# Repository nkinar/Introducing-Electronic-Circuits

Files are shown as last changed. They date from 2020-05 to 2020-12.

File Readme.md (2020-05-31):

# Introducing Electronic Circuits and Hydrological Models to Postsecondary Physical Geography Students: Systems Science, Circuit Theory, Construction and Calibration
## by Nicholas J. Kinar
*Journal of Geoscience Communication (GC)*

## What is it?

* The download contains directories providing circuit board design files and feedback data.
Files are provided "as is" and should be checked before use in a specific application.

* Please see the associated paper for additional information.  

* Cost and part numbers in the Excel bill of material (BOM) spreadsheets are current at the time of
writing.  The cost is in Canadian dollars.  Most part numbers for passive components (resistors and capacitors)
can be substituted.  The BOM does not include materials used for kit packaging: ESD bags, plastic bags and
ESD foam used to protect IC pins.

* Bags, labelling machines and labels can be sourced from Uline (or a similar supplier):
<https://www.uline.ca/> or
<https://www.uline.com/>

* At the time of writing, an educational license is available from Altium and
the DFM Now! software can be downloaded as a no-cost license.  See the table
below for further details.

* All circuit board designs are licensed under the open hardware CERN OHL license:
http://cern.ch/cern-ohl

* All source code is provided under the GNU GPL v3:
https://www.gnu.org/licenses/gpl-3.0.en.html

## FILES

Bolded entries in the table indicate parent directories.  Non-bolded
entries indicate subdirectories.

| Directory   |     Description  |
|----------|:-------------:|
| **class-sensor-pcb-design-files** | Parent directory with design files for the class RH/temperature/pyranometer circuit|
| altium |   Design files in Altium designer format (https://www.altium.com/)  |  
| bom | Bill of Materials (Excel) |
|code	| Code for Atmel AVR microcontroller (Atmel Studio)|
|gerber	| Gerber files |
|schematic	| Schematic (PDF) |
|**feedback data**	| Directory with in-class feedback|
|**feedback-data-sleq**	| Feedback data from the SLEQ survey|
|**water-sensor-pcb-design-files**	| Directory with design files for the class water detection circuit|
|altium	|						Design files in Altium designer format (https://www.altium.com/)|
|bom |								Bill of Materials (Excel)|
|gerber |							Gerber files|
|schematic |						Schematic (PDF)|

## GERBER FILES README AND MAPPING

1.	These are 2 layer PCBs.
2.	Round up drill size to the next available drill (free or non-free) if required.
3.	Soldermask on both sides of the PCB
4.	Silkscreen on both sides of the PCB
5.	DFM Now! software can be used for Gerber preview (https://www.numericalinnovations.com/)
6.	gerbv also works well as Gerber preview software (http://gerbv.sourceforge.net/)

| Layer Extension   |     Layer Description  |
|----------|:-------------:|
|.GTO|                Top Overlay |                            
|.GTS|                Top Solder  |                            
|.GTL|                Top Layer    |                           
|.GBL|                Bottom Layer      |                      
|.GBS|                Bottom Solder   |                        
|.GM1|                Mechanical 1   |                         
|.GPT|                Top Pad Master      |                    
|.GPB|                Bottom Pad Master|
|.DRR| 				NC Drill File Report|
|.TXT|				NC Drill File|

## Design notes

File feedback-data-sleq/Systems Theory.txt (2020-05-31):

While I a still confused about it, I think it is good knowledge to know.

I can see better connection between different processes involved in evironal sciences

Environmental sciences are all about systems. Because of this class I think broader now when reviewing a system.

I see systems theory as an integral framework of how we understand natural phenomena in that it is how we can turn readings
from instruments and synthesize them into models that describe a natural system with distinct boundary conditions and specific
inputs.

It's important to understand every component of the environment with great detail. You can use these systems as sub systems to
understand the greater picture.

very important

Understanding systems and the theory behind how they work is important to understanding the natural environment for a variety of
environmental studies.

I never thought about the importance of these systems before this class, so I suppose it opened my eyes to the complexity of
research

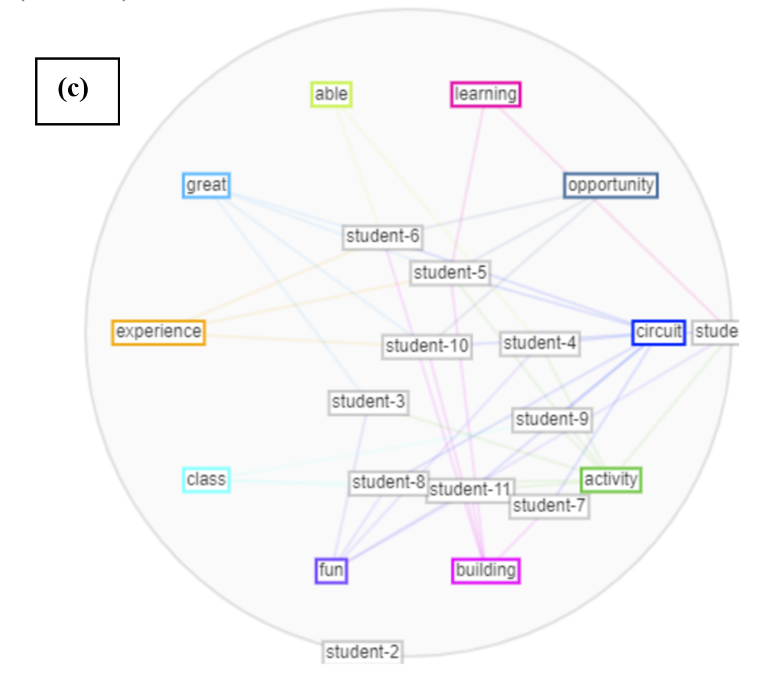
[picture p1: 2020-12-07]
feedback-data/mandala.PNG

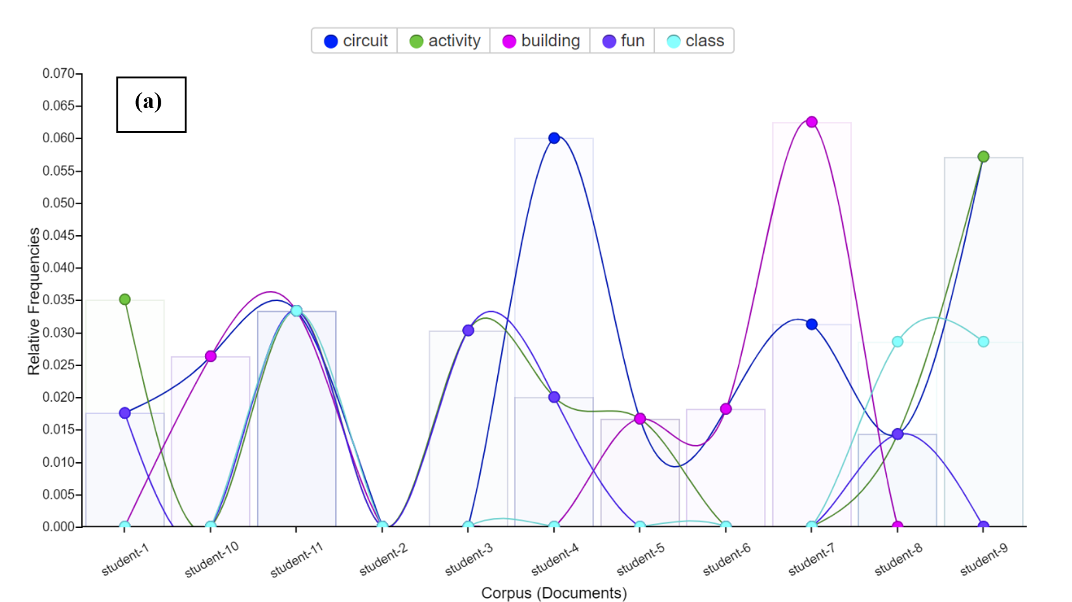
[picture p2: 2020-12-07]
feedback-data/trends.PNG

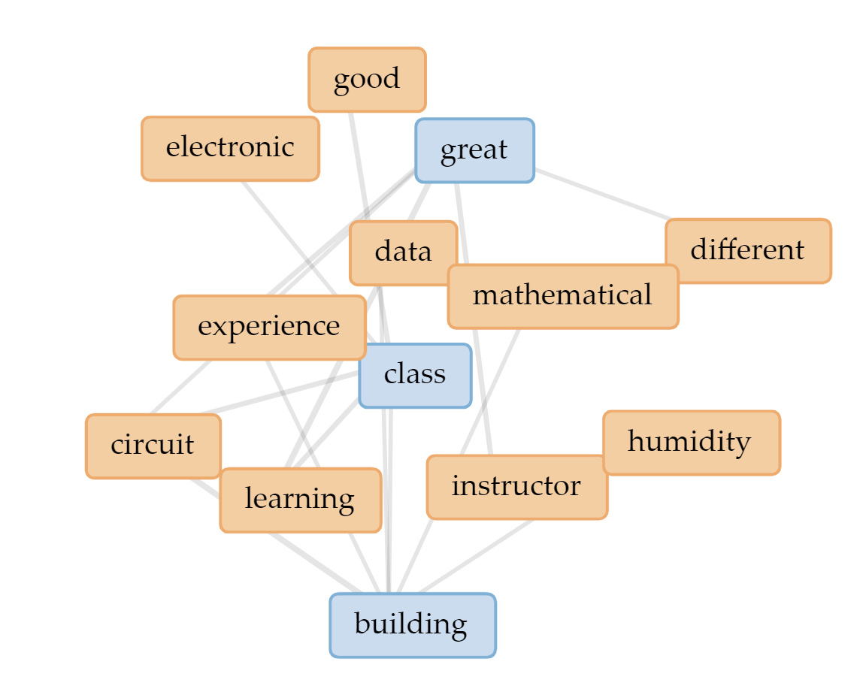
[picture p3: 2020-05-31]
feedback-data-sleq/links.PNG

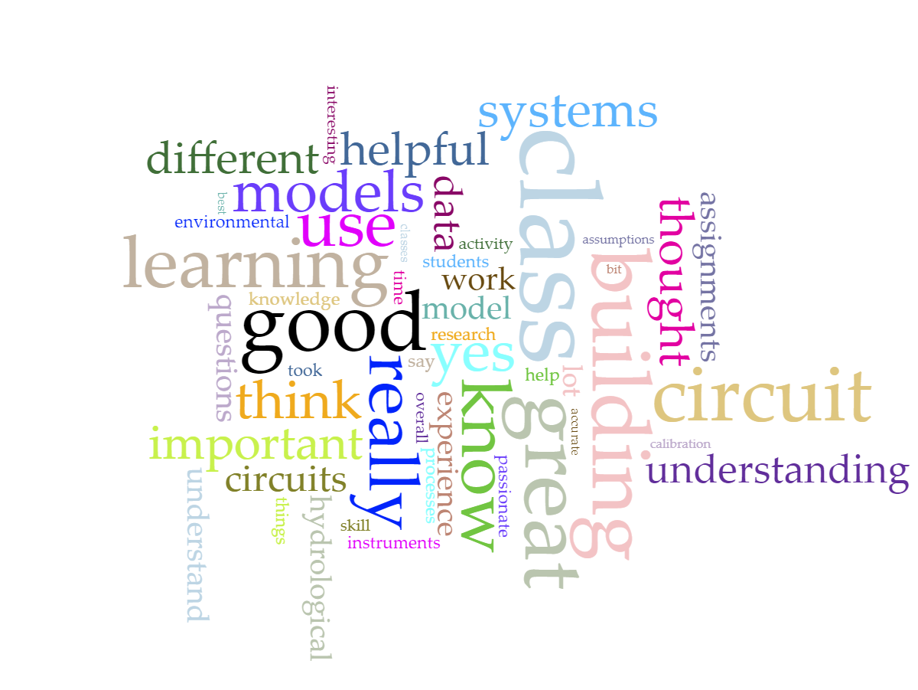
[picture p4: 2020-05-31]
feedback-data-sleq/cirrus.PNG

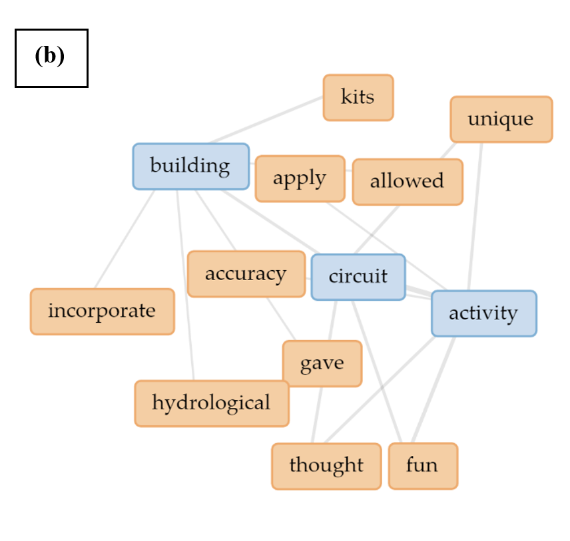
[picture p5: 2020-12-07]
feedback-data/links.PNG

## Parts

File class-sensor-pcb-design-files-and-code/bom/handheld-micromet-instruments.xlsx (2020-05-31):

Line # | Qty | Manufacturer P/N | Manufacturer | Distributor P/N | Distributor | Description
1 | 1 | BK Precision 725 | BK Precision | BK725-ND | Digikey.ca | Humidity/Temperature Meter
2 | 1 | TPI 565C1 | TPI (Test Products Int) | 290-1975-ND | Digikey.ca | Hot wire anemometer / Temperature Meter
3 | 1 | SP505 | Extech | SP505-ND | Digikey.ca | Solar power (flux) Meter
4 | 1 | SD-1128 | Reed Instruments | B008S0AKJA | Amazon.ca | Light meter

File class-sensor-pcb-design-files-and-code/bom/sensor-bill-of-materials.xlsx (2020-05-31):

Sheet: Totals
Qty | 30
 |  | Currency
Option 1 | Relative Humidity and Temperature
Base Cost | 16.97 | CND
Relative Humidity | 8.01 | CND
TOTAL per student | $24.98 | CND
Option 2 | Pyranometer
Base Cost | 16.97 | CND
Pyranometer Sensor | 13.59 | CND
TOTAL per student | $30.56 | CND
Option 3 | Both RH/T and Pyranometer
Base Cost | 16.97 | CND
Both Sensors | 22.2 | CND
TOTAL per student | $39.17 | CND
Tools and Materials
TOTAL | $156.20 | CND
PCBs
TOTAL | $66.60 | CND

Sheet: Base Kit
Line # | Designator | Qty | Total Order | Manufacturer P/N | Manufacturer | Total | Distributor P/N | Distributor | Description | Unit Cost (CND) | Total Cost (CND) | Comments | Price per package | Currency Conversion | Package (CND) | Total Number | Cost per unit (CND)
1 | U1 | 1 | 0 | ERM802SN-1 | EastRising | 0 | ERM802SN-1 | buydisplay.com | LCD Display | 2.75 | 2.75 | LCD display | 2.07 | 1.33 | 2.7531 | 1 | 2.75
2 | NA | 1 | 0 | B0784FMY9J | abcGOODefg | 0 | B0784FMY9J | Amazon.ca | 9V battery holder | 1.75 | 1.75 | Holds 9V battery on PCB | 13.99 | 1 | 13.99 | 8 | 1.75
3 | NA | 1 | 0 | PCB | allpcb.com | 0 | PCB | allpcb.com | Custom PCB for circuit | 2.22 | 2.22 | PCB for circuit | 50 | 1.33 | 66.5 | 30 | 2.22
4 | NA | 1 | 0 | Battery | Amazon Basics | 0 | B00MH4QM1S | Amazon.ca | 9v Battery | 1.66 | 1.66 | Battery to run circuit
5 | C1,C16,C17 | 3 | 0 | ECE-A1HKS100 | Panasonic Electronic Components | 0 | P997-ND | Digikey | CAP ALUM 10UF 20% 50V RADIAL | 0.04 | 0.13 | Decoupling capacitor
6 | C2,C3,C4 | 3 | 0 | A104K15X7RF5TAA | Vishay BC Components | 0 | 1109PHCT-ND | Digikey | CAP CER 0.1UF 50V X7R AXIAL | 0.24 | 0.71 | Decoupling capacitor
7 | R1 | 1 | 0 | 3306P-1-502 | Bourns Inc. | 0 | 3306P-502-ND | Bourns | TRIMMER 5K OHM 0.2W PC PIN TOP | 0.55 | 0.55 | Trimpot for LCD contrast
8 | R2,R3,R4 | 3 | 0 | CF14JT10K0 | Stackpole Electronics Inc | 0 | CF14JT10K0CT-ND | Digikey | RES 10K OHM 1/4W 5% AXIAL | 0.03 | 0.10 | Pullup resistors
9 | L1 | 1 | 0 | 78F100J-TR-RC | Bourns Inc. | 0 | 78F100J-TR-RCCT-ND | Digikey | FIXED IND 10UH 370MA 750 MOHM TH | 0.40 | 0.40 | Inductor for LC filter
10 | U6 | 1 | 0 | ATMEGA168PA-PU | Microchip Technology | 0 | ATMEGA168PA-PU-ND | Digikey | IC MCU 8BIT 4KB FLASH 28DIP | 2.50 | 2.50 | Microcontroller
11 | C5,C7 | 2 | 0 | K330J15C0GF5TH5 | Vishay BC Components | 0 | BC1036CT-ND | Digikey | CAP CER 33PF 50V C0G/NP0 RADIAL | 0.25 | 0.50 | Crystal resonator circuit capacitors
12 | X1 | 1 | 0 | ATS080B-E | CTS-Frequency Controls | 0 | CTX917-ND | Digikey | CRYSTAL 8.0000MHZ 18PF T/H | 0.48 | 0.48 | Crystal for microcontroller
13 | P2 | 1 | 0 | M20-9980346 | Harwin Inc. | 0 | 952-2121-ND | Digikey | CONN HEADER VERT 6POS 2.54MM | 0.33 | 0.33 | Programming header
14 | J2 | 1 | 0 | JS202011CQN | C&K | 0 | 401-2001-ND | Digikey | SWITCH SLIDE DPDT 300MA 6V | 0.60 | 0.60 | Power switch
15 | D2 | 1 | 0 | BAT85S-TAP | Vishay | 0 | BAT85S-TAPCT-ND | Digikey | DIODE SCHOTTKY 30V 200MA DO35 | 0.46 | 0.46 | Diode
16 | U13 | 1 | 0 | LP2950-50LPRE3 | Texas Instruments | 0 | 296-20933-1-ND | Digikey | IC REG LINEAR 5V 100MA TO92-3 | 0.61 | 0.61 | Linear regulator
18 | NA | 4 | 0 | 91772A057 | McMaster-Carr | 0 | 91772A057 | McMaster-Carr | #0 bolts for display | 0.10 | 0.40 | Bolts for display | 7.87 | 1.33 | 10.4671 | 100 | 0.1
19 | NA | 4 | 0 | 90107A001 | McMaster-Carr | 0 | 90107A001 | McMaster-Carr | #0 washer for display | 0.03 | 0.12 | Washer for display | 2.36 | 1.33 | 3.1388 | 100 | 0.03
20 | NA | 4 | 0 | 91841A115 | McMaster-Carr | 0 | 91841A115 | McMaster-Carr | #0 hex nut for display | 0.10 | 0.40 | Hex nut | 7.85 | 1.33 | 10.4405 | 100 | 0.1
21 | NA | 3 | 0 | 90353A486 | McMaster-Carr | 0 | 90353A486 | McMaster-Carr | M2 bolts for battery | 0.05 | 0.15 | Bolts for battery | 4.1 | 1.33 | 5.453 | 100 | 0.05
22 | NA | 3 | 0 | 91166A180 | McMaster-Carr | 0 | 91166A180 | McMaster-Carr | M2 washer for battery | 0.02 | 0.06 | Washer for battery | 1.57 | 1.33 | 2.0881 | 100 | 0.02
23 | NA | 3 | 0 | 90591A265 | McMaster-Carr | 0 | 90591A265 | McMaster-Carr | M2 hex nut for battery | 0.03 | 0.09 | Hex nut for battery | 2.08 | 1.33 | 2.7664 | 100 | 0.03
 |  |  |  |  |  |  |  |  |  | TOTAL | 16.97

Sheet: RH-T kit
Line # | Designator | Qty | Total Order | Manufacturer P/N | Manufacturer | Total Qty | Distributor P/N | Distributor | Description | Unit Cost (CND) | Total Cost (CND) | Comments | Price per package | Currency Conversion | Package (CND) | Total Number | Cost per unit (CND)
1 | NA | 8 | 0 | B07FKFQQC9 | GikFun | 0 | B07FKFQQC9 | Amazon.ca | Jumpers | 0.05 | 0.40 | Jumpers for calibration | 9.99 | 1 | 9.99 | 200 | 0.05
2 | C6,C10 | 2 | 0 | A104K15X7RF5TAA | Vishay BC Components | 0 | 1109PHCT-ND | Digikey | CAP CER 0.1UF 50V X7R AXIAL | 0.24 | 0.47 | Decoupling capacitor
3 | U7 | 1 | 0 | MCP23008-E/P | Microchip Technology | 0 | MCP23008-E/P-ND | Digikey | IC I/O EXPANDER I2C 8B 18DIP | 1.34 | 1.34 | I/O expander
4 | P5 | 1 | 0 | PREC008DAAN-RC | Sullins Connector Solutions | 0 | S2012EC-08-ND | Digikey | CONN HEADER VERT 16POS 2.54MM | 0.41 | 0.41 | Header
5 | U10 | 1 | 0 | COM1700/AM2320 | AOSONG/Pimoroni | 0 | 1778-1179-ND | Digikey | AM2320 DIGITAL TEMPERATURE AND H | 5.39 | 5.39
 |  |  |  |  |  |  |  |  |  | TOTAL | 8.01

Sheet: Pyranometer kit
Line # | Designator | Qty | Total Qty | Manufacturer P/N | Manufacturer | Total Qty | Distributor P/N | Distributor | Description | Unit Cost (CND) | Total Cost (CND) | Comments | Price per package | Currency Conversion | Package (CND) | Total Number | Cost per unit (CND)
1 | NA | 32 | 1280 | B07FKFQQC9 | GikFun | 1280 | B07FKFQQC9 | Amazon.ca | Jumpers | 0.05 | 1.60 | Jumpers for calibration | 9.99 | 1 | 9.99 | 200 | 0.05
2 | C8,C9,C12,C18 | 4 | 160 | A104K15X7RF5TAA | Vishay BC Components | 160 | 1109PHCT-ND | Digikey | CAP CER 0.1UF 50V X7R AXIAL | 0.24 | 0.95 | Decoupling capacitor
3 | U8,U9 | 2 | 80 | MCP23017-E/SP | Microchip Technology | 80 | MCP23017-E/SP-ND | Digikey | IC I/O EXPANDER I2C 16B 28SDIP | 1.57 | 3.15 | Expander
4 | P4,P6 | 2 | 80 | PREC016DAAN-RC | Sullins Connector Solutions | 80 | S2012EC-16-ND | Digikey | CONN HEADER VERT 32POS 2.54MM | 0.74 | 1.48 | Header
5 | C13,C14,C15 | 3 | 120 | ECE-A1HKS100 | Panasonic Electronic Components | 120 | P997-ND | Digikey | CAP ALUM 10UF 20% 50V RADIAL | 0.04 | 0.13 | Decoupling capacitor
6 | U11 | 1 | 40 | TL072IP | Texas Instruments | 40 | 296-14997-5-ND | Digikey | IC OPAMP JFET 2 CIRCUIT 8DIP | 0.87 | 0.87 | JFET op amp
7 | C11 | 1 | 40 | FA28C0G1H010CNU06 | TDK Corporation | 40 | 445-180705-1-ND | Digikey | CAP CER 1PF 50V C0G RADIAL | 0.32 | 0.32 | Feedback loop cap
8 | R5 | 1 | 40 | MFP-25BRD52-910R | Yageo | 40 | 910ADCT-ND | Digikey | RES 910 OHM 1/4W 0.1% AXIAL | 0.54 | 0.54 | Feedback resistor
9 | R6,R7 | 2 | 80 | RNF14FTD1K00 | Stackpole Electronics Inc | 80 | RNF14FTD1K00CT-ND | Digikey | RES 1K OHM 1/4W 1% AXIAL | 0.07 | 0.14 | Feedback resistor
10 | D4 | 1 | 40 | BAT85S-TAP | Vishay | 40 | BAT85S-TAPCT-ND | Digikey | DIODE SCHOTTKY 30V 200MA DO35 | 0.44 | 0.44 | Clamp diode
11 | D1 | 1 | 40 | BPW34 | OSRAM Opto | 40 | 475-1070-ND | Digikey | SENSOR PHOTODIODE 850NM 2DIP | 1.17 | 1.17 | Photodiode
12 | U12 | 1 | 40 | LMC7660IN/NOPB | Texas Instruments | 40 | LMC7660IN/NOPB-ND | Digikey | IC REG CHARGE PUMP INV 8DIP | 1.67 | 1.67 | Negative voltage inverter
13 | NA | 1 | 40 | 8545K12 | McMaster-Carr | 40 | 8545K12 | McMaster-Carr | Teflon sheet | 1.08 | 1.08 | Diffuser | 12.22 | 1.33 | 16.2526 | 15 | 1.08
14 | NA | 1 | 40 | 48925K92 | McMaster-Carr | 40 | 48925K92 | McMaster-Carr | 3/4" pipe white | 0.07 | 0.07 | Holder for diffuser | 3.3 | 1.33 | 4.389 | 60 | 0.07
 |  |  |  |  |  |  |  |  |  | TOTAL | 13.59

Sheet: Hybrid
Line # | Designator | Qty | Total Qty | Manufacturer P/N | Manufacturer | Distributor P/N | Distributor | Description | Unit Cost (CND) | Total Cost (CND) | Comments | Price per package | Currency Conversion | Package (CND) | Total Number | Cost per unit (CND)
1 | J1 | 1 | 40 | JS202011CQN | C&K | 401-2001-ND | Digikey | SWITCH SLIDE DPDT 300MA 6V | 0.60 | 0.60 | Selector switch
 |  |  |  |  |  |  |  |  | TOTAL | 0.60

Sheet: Tools and Materials
Line # | Qty | Manufacturer P/N | Manufacturer | Distributor P/N | Distributor | Description | Unit Cost (CND) | Total Cost (CND) | Comments | Price per package | Currency Conversion | Package (CND) | Total Number | Cost per unit (CND)
1 | 5 | FX-901/P | American Hakko Products, Inc. | 1691-1084-ND | Digikey | SOLDERING IRON 6W 6V 5W 4.8V | 48.76 | 243.80 | Soldering iron for each group (provided)
2 | 1 | 673829 | Multicore | 82-124-ND | Digikey | Solder Spool | 111.33 | 111.33 | Spool of solder (1 m per student)
3 | 30 | 300810 | SCS | SCP315-ND | Digikey | ESD Bags | 0.40 | 12.00 | ESD bag for holding circuits
4 | 30 | SC-203 | Rugged Blue | SFTEYSG1000033177 | Discount Safety Gear | Safety Glasses | 1.16 | 34.80 | Safety glasses for eye protection | 0.87 | 1.33 | 1.1571 | 1 | 1.16
5 | 48 | Energizer Max | Energizer | Energizer Max | Amazon.ca | AA batteries | 0.56 | 26.88 | Batteries for soldering irons
6 | 5 | TC205 | Apex Tool Group | TC205-ND | Digikey | Solder Sponge | 2.13 | 10.65 | Sponge for soldering
7 | 5 | Organizer | Dollar Tree | Organizer | Dollar Tree | Plastic organizer | 1.25 | 6.25 | Plastic container for holding sponge
8 | 5 | Tool Box | Dollar Tree | Tool Box | Dollar Tree | Plastic toolbox | 1.25 | 6.25 | Toolbox for organizing materials for each group
9 | 5 | Tape | Dollar Tree | Tape | Dollar Tree | Scotch tape | 1.25 | 6.25 | Tape for holding parts in place during soldering
10 | 5 | Bottle | Dollar Tree | Bottle | Dollar Tree | Bottle | 1.25 | 6.25 | Bottle for holding water to wet soldering sponge
11 | 5 | Screwdriver Set | Dollar Tree | Screwdriver Set | Dollar Tree | Small screwdriver set | 1.25 | 6.25 | Small screwdriver set for tightening screws
12 | 5 | Pliers | Dollar Tree | Pliers | Dollar Tree | Long-nose pliers | 1.25 | 6.25 | Long nose pliers for bending leads and holding nuts
13 | 3 | Superglue | LePage | Superglue | Amazon.ca | Superglue | 7.29 | 21.87 | qty 4 superglue for assembling pyranometer
14 | 5 | Cutters | Dollarama | Cutters | Dollarama | Cutters | 2.50 | 12.50 | Cutters for trimming leads on parts
15 | 5 | 21-1585 | MCM | 21-1585 | Newark | IC Pin straightener | 7.57 | 37.85 | Pin straighener for IC
16 | 25 | 038-0100 | Multicomp | 038-0100 | Newark | Conductive Foam | 1.25 | 31.25 | Conductive Foam for storing ICs
17 | 5 | 10454189 | Craft Smart | 10454189 | Michaels | Small Scissors | 3.29 | 16.45 | Used for opening batteries and removing plastic
 | 1 | 2405 | Paper Pro | 2405 | Amazon.ca | Hole punch | 4.99 | 4.99 | Used for creating air holes in bags
 |  |  |  |  |  |  | TOTAL | 156.20 | Materials (not including soldering irons and solder)
GROUPS
5

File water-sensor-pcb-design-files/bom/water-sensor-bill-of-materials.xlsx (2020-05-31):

Line # | Designator | Qty | Total Order | Manufacturer P/N | Manufacturer | Total | Distributor P/N | Distributor | Description | Unit Cost (CND) | Total Cost (CND) | Comments
1 | U1 | 1 | 1 | SN74HC14N | Texas Instruments | 1 | 296-1577-5-ND | Digikey | IC INVERTER SCHMITT 6CH 14DIP | 0.93 | 0.93
2 | R1 | 1 | 1 | CFR-25JB-52-1M | Yageo | 1 | 1.0MQBK-ND | Digikey | RES 1M OHM 1/4W 5% AXIAL | 0.16 | 0.16
3 | R2 | 1 | 1 | CF14JT150R | Stackpole Electronics Inc | 1 | CF14JT150RCT-ND | Digikey | RES 150 OHM 1/4W 5% AXIAL | 0.16 | 0.16
4 | D1 | 1 | 1 | WP7113LGD | Kingbright | 1 | 754-1265-ND | Digikey | LED GREEN DIFFUSED T-1 3/4 T/H | 0.73 | 0.73
5 | J2 | 1 | 1 | 2462 | Keystone Electronics | 1 | 36-2462-ND | Digikey | BATTERY HOLDER AA 2 CELL PC PIN | 1.85 | 1.85
6 | B | 2 | 2 | LR6XWA/B | Panasonic - BSG | 2 | P646-ND | Digikey | AA Battery | 0.60 | 1.20
7 | PCB | 1 | 1 | PCB | https://www.allpcb.com/ | 1 | PCB | All PCB | PCB for project | 0.84 | 0.84
8 | Bolts | 2 | 2 | 92010A787 | McMaster Carr | 2 | 92010A787 | McMaster Carr | M3 Flat head screw | 0.80 | 1.60
9 | Nuts | 2 | 2 | 91828A211 | McMaster Carr | 2 | 92010A787 | McMaster Carr | M3 nut | 0.80 | 1.60
 |  |  |  |  |  |  |  |  |  | TOTAL | 9.07

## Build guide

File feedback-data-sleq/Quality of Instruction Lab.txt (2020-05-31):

There was not really any lab sections for this class but when building the circuit he was very good.

Great instructor, passionate about the topics and always finds a way to make them interesting

Great job

Wonderful support if we messed up our circuit pieces instead of saying "uh oh sorry cant help you with that guess your gonna get a
zero" he was willing to go the extra mile and take time out of his busy schedule to repair the circuits that had technical issues. He
even took videos to show us so we would know how to repair them in the future if we needed.

Very well–organized and well–supplied circuit–building sessions. Assistance from Dr. Kinar was indispensable. Having the circuit
kits be in individual ziplock bags with clearly demarcated parts greatly improved the efficiency of the building process.
It was cool having multiple guest lecturers. It showed us different aspects of the field of hydrology. Nicholas would go out of his way
to help students out.

He was very helpful and is very passionate about what he teaches. One of the best instructors I have ever had. I really appreciate his
passion and how much he cares about our actual learning in this class.

Great!

The labs were very hands on and helped my learning a lot.

Nick was very nice, accessible, and understanding. I have no bad things to say about his class.

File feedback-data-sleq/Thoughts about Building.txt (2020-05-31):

This was the best part of the class! Really respected all the effort put into this on Professor Kinar's part. Lots of fun.

Great experience, something new and different to any other classes I have take before

Loved it

I really enjoyed the aspect of being able to use hands on learning with the circuits instead of just learning through presentations.

The calibration of the pyranometer had me a little stumped at first.

I thought it was very helpful and relevant to the concept of models as discussed in the class notes, although I feel like the circuit
building took up so much of the course timeline that it comes at a detriment to the discussions of concepts and theories of
hydrological phenomena.

I thought it was really cool. I never thought about the importance of the construction of an electronic circuit until this class. Shows
how accurate and non–accurate the devices used to collected field data can be.

It was interesting. I never thought I would be building a circuit within my university journey, but I am happy to have experienced it.

I found it very interesting. As I have never done it before, I found it to be a great learning experience and introduction to circuit
building. I can now say that I have experience with very basic circuit building, which I think is a great skill to have.

very unique activity! I would recommend continuing the activity in upcoming classes, as it is something unlike any other class.

Building the electronic circuits was a very fun learning activity that helped me learn a new skill set. Overall the building of the circuit
took up too much class time but having something that I could take home and use to collect data was great.

It was fun and different. The only thing is it took quite a bit of time away from the class materials.

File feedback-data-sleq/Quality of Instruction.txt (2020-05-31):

Very passionate, concepts of what is being taught or what students are supposed to take home from the lectures is not always clear
though. Very helpful, however, when it came to assignments and the ahnds on tasks.

Great instructor, passionate about the topics and always finds a way to make them interesting

BEST PROFESSOR EVER will definitely recommend his classes to others. He is patient, helpful and always has the time for us
students. He goes in depth on different theories and has no problem answering any questions we have on the topic if it at first goes
over our heads. Also liked how he brought examples of equipment to class for us to inspect.

Good concise slides, and a good amount of elaboration on the slides from Dr. Kinar.

Nicholas was awesome. Super enthusiastic about us learning the subject he really enjoys himself. He was very good and making
us understand key concepts.

Great. He really cares about his students. He's always available to help. Near the end of the course he went through material a little
faster than I expected, but I understand he's trying to get through material.

Very good instruction.

Great!

Overall the instructor was very knowledgeable and went in depth on a variety of topics

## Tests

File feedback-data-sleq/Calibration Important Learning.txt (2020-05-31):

Yes, I do if you are wanting to do a degree in hydrology or a minor in water science. It is something that could be applied after
university.

Yes, it is a useful skill to have when doing research or applying for jobs.

Yes as they are useful in future research

Yes I do, as scientists we should know how to do field and lab exercises and how to calibrate, maintain and use our own machines.
Yes, I thought they were very helpful at giving a scaled down conceptualization of how scientific models work. Seeing the nonsense
uncalibrated data from the T/RH and pyranometers and figuring out the calibration coefficient using high–school math was helpful
in understanding how theory must be applied to instruments.

Yes they are. It teaches you how you can create your own model and the accuracy of the model.

Sure. Before this class I did not think so because I did not know. Now that I have learnt more about it, I would say its important.

Yes I do think so because environmental scientists use many electronic instruments involving circuits to measure certain
hydrological processes. I think it is a good skill to have if you can know how the circuits themselves work and maybe even be able to
develop your own basic instruments.

Yes. Because those are things we should have a good understanding of if we plan on doing research work. We need to know how
to troubleshoot, or what may be going wrong, or what things we should be considering. Circuits are a good use for analog models,
and it is definitely important to be familiar with them.

Instrument calibration is very important to environmental scientists because it ensures accurate data collection.

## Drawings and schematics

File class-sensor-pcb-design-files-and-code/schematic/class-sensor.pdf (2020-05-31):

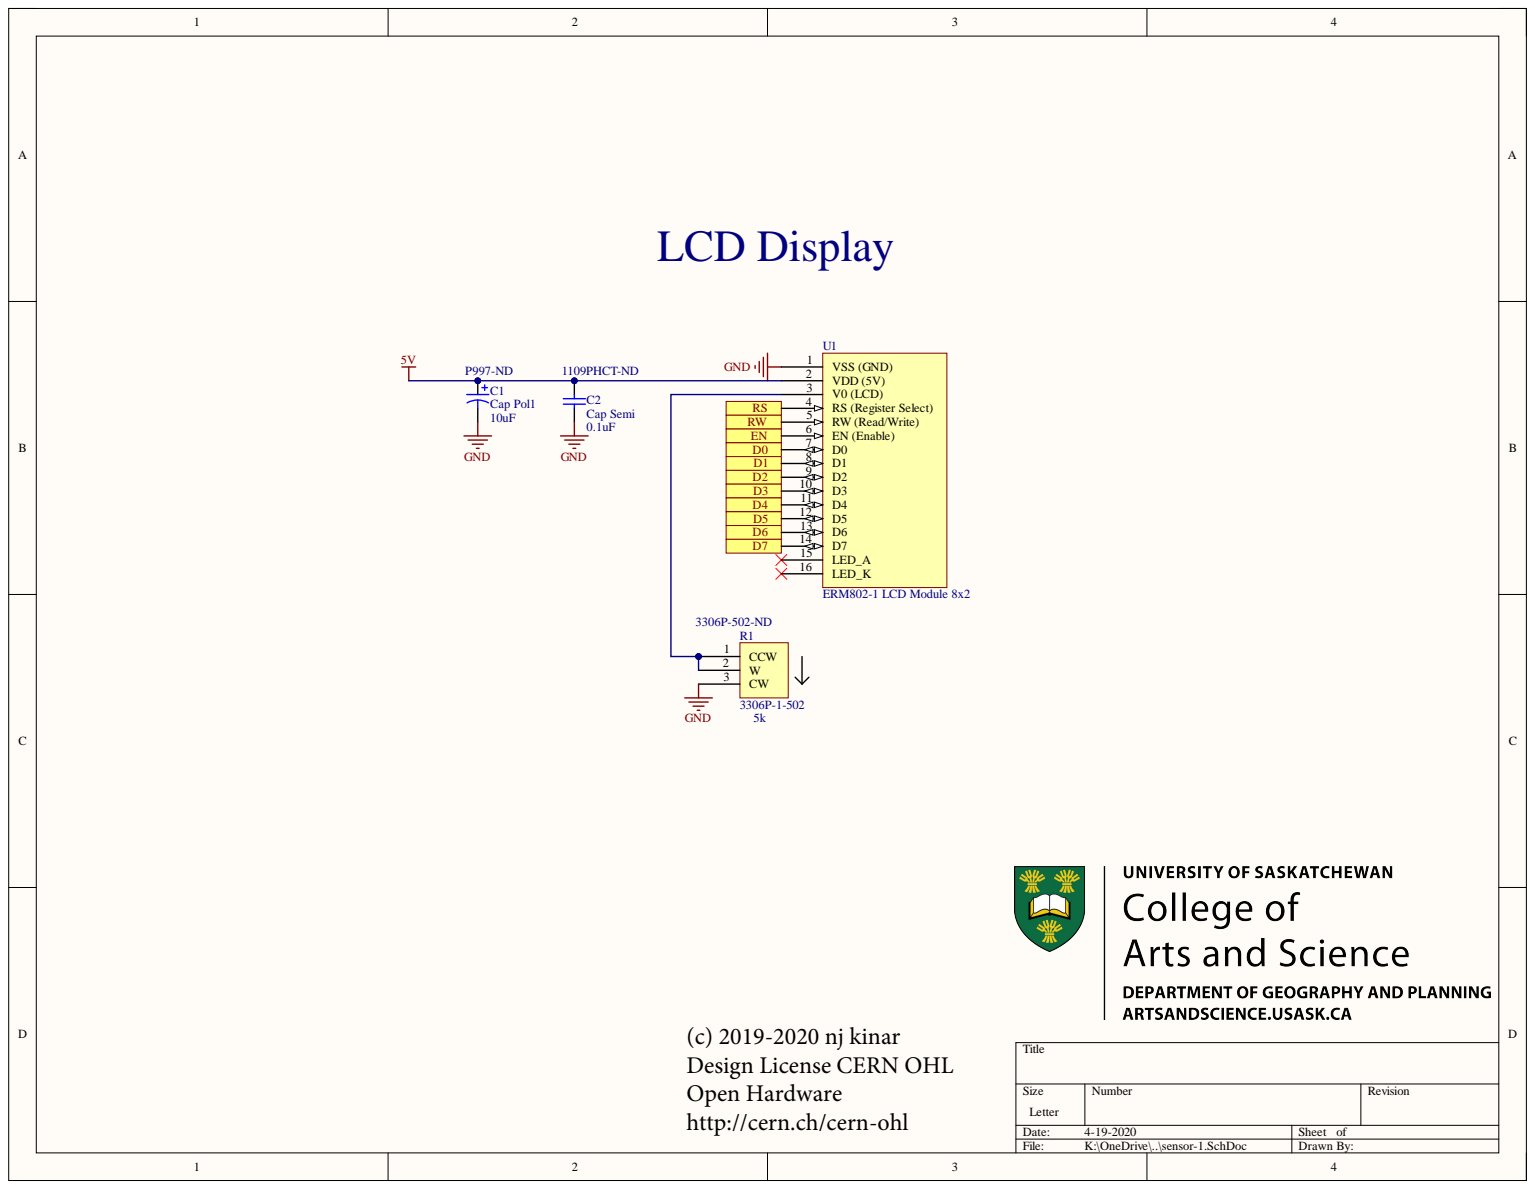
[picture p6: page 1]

(c) 2019-2020 nj kinar
Design License CERN OHL
Open Hardware
http://cern.ch/cern-ohl

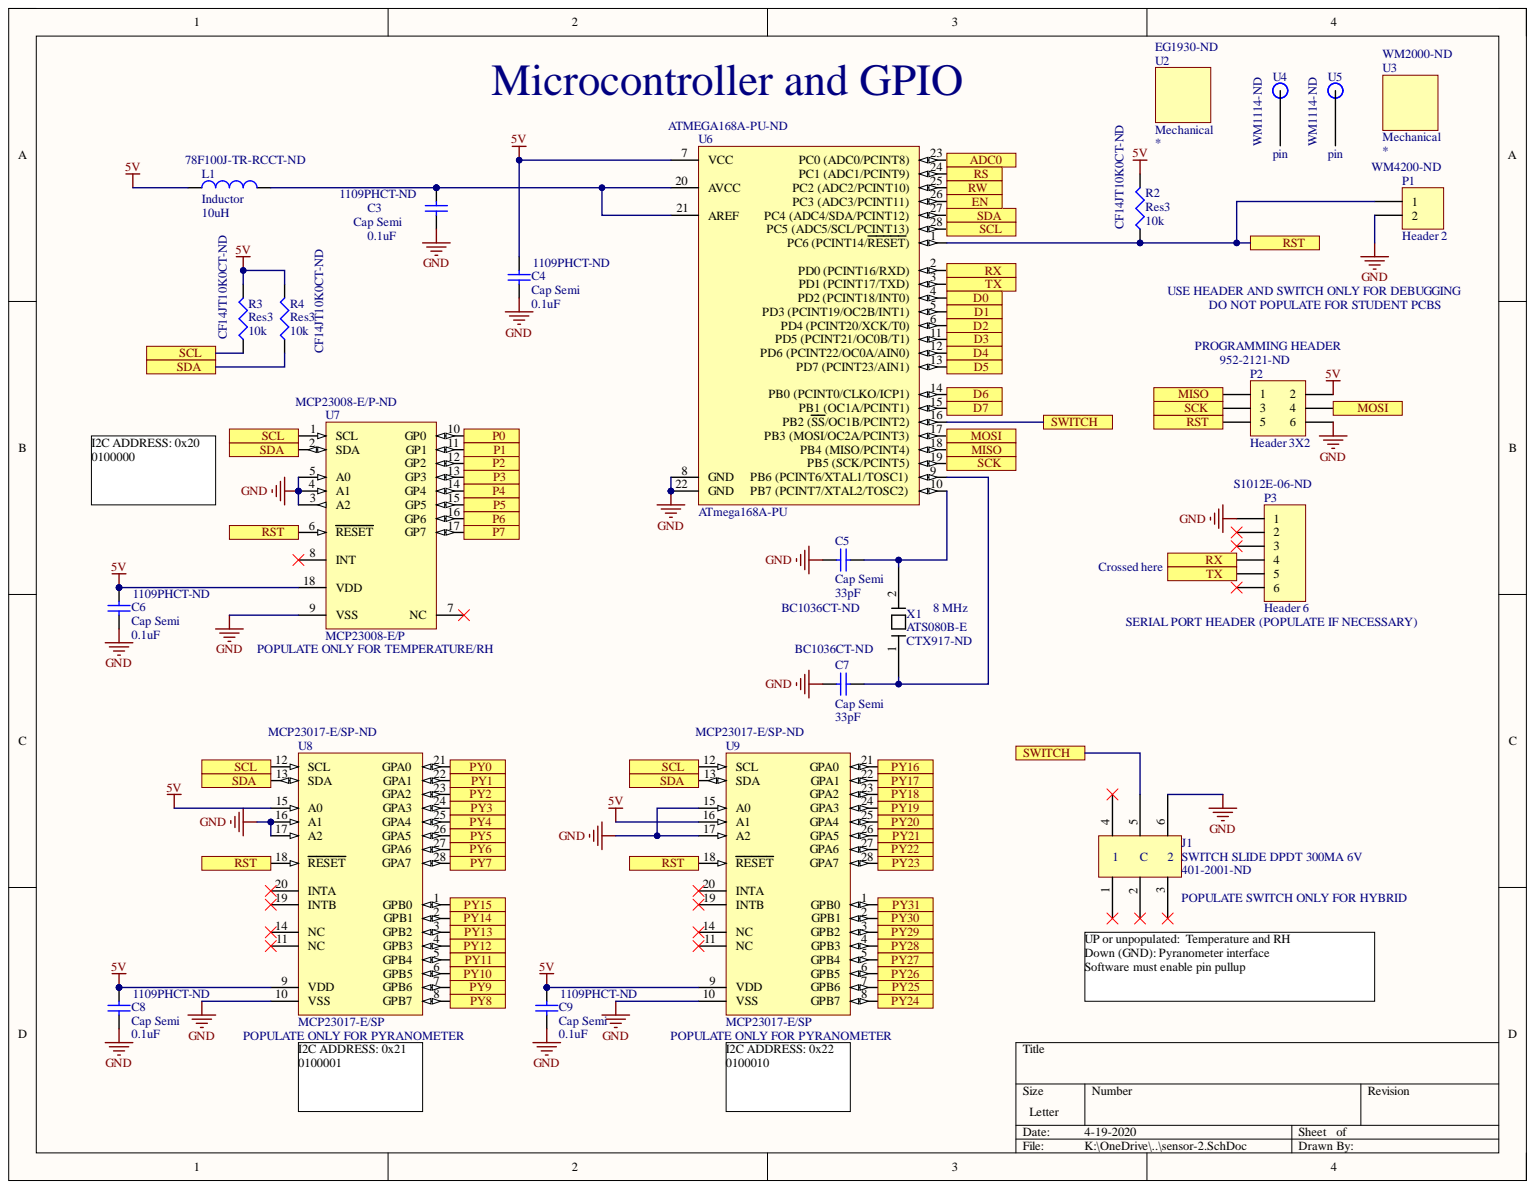
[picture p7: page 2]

USE HEADER AND SWITCH ONLY FOR DEBUGGING

DO NOT POPULATE FOR STUDENT PCBS

SERIAL PORT HEADER (POPULATE IF NECESSARY)

POPULATE ONLY FOR TEMPERATURE/RH

POPULATE SWITCH ONLY FOR HYBRID

UP or unpopulated: Temperature and RH
Down (GND): Pyranometer interface
Software must enable pin pullup

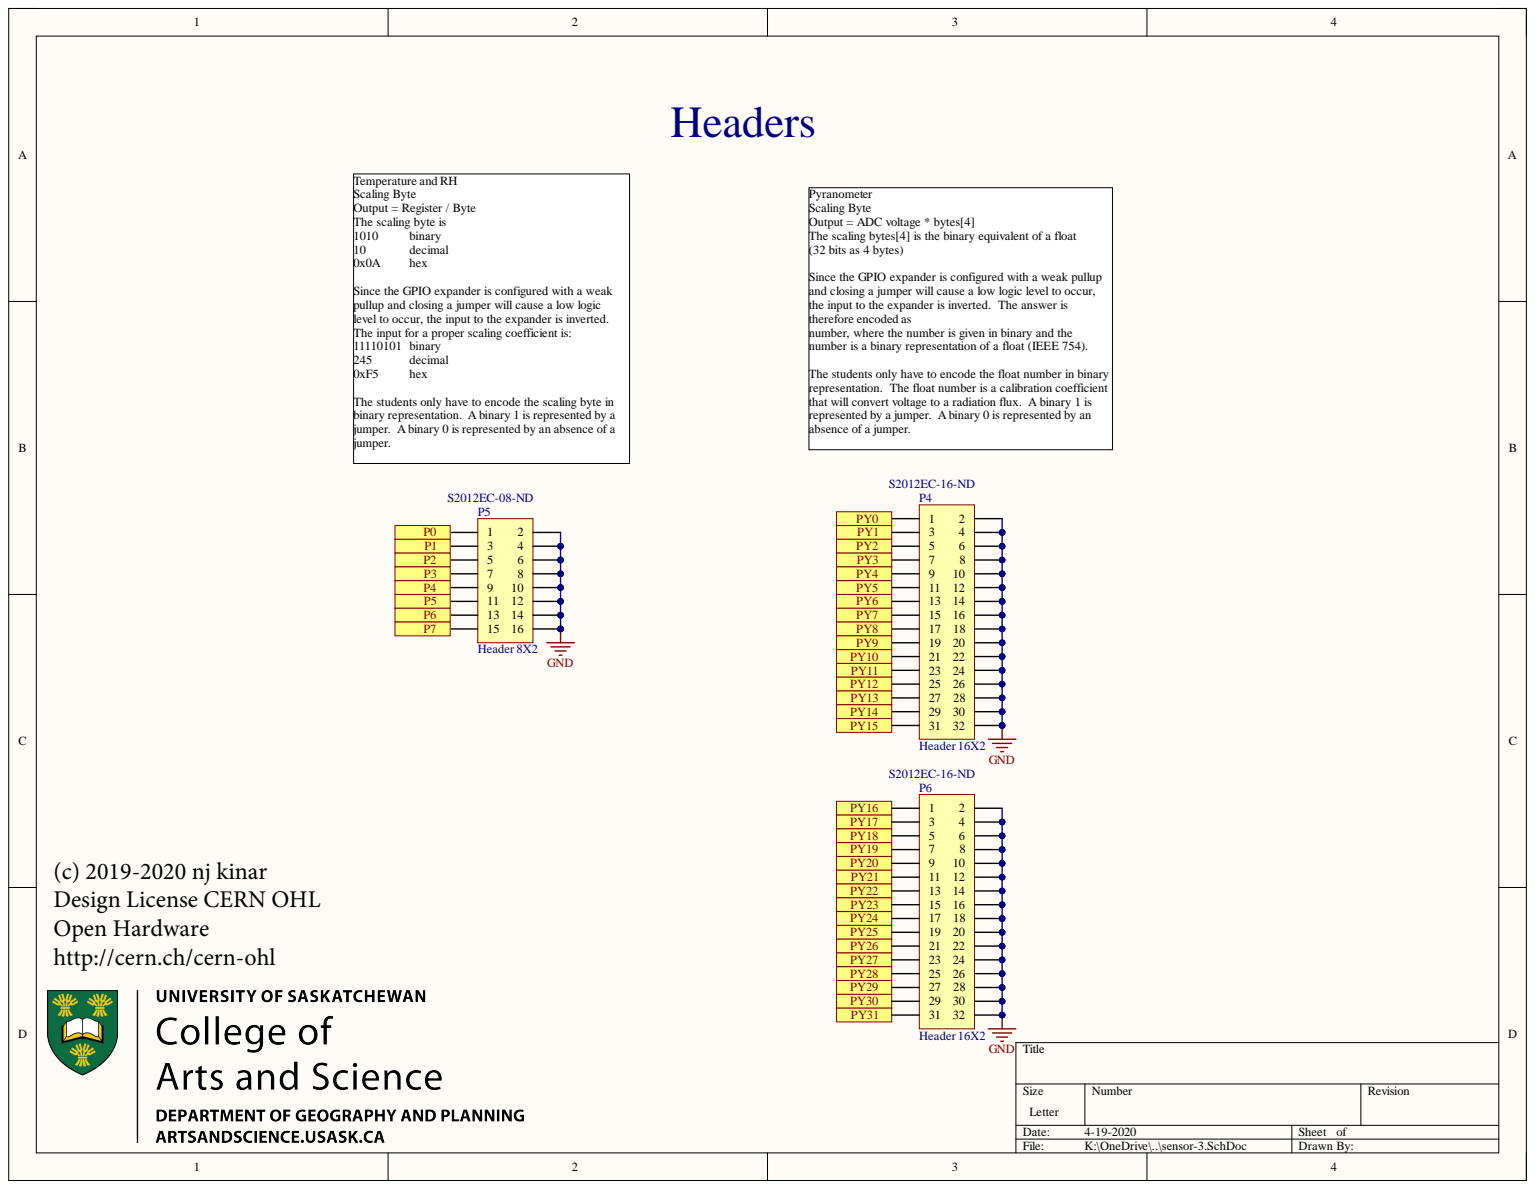
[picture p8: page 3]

Temperature and RH
Scaling Byte
Output = Register / Byte
The scaling byte is

Pyranometer
Output = ADC voltage * bytes[4]
The scaling bytes[4] is the binary equivalent of a float
(32 bits as 4 bytes)

Since the GPIO expander is configured with a weak pullup
and closing a jumper will cause a low logic level to occur,
the input to the expander is inverted. The answer is
therefore encoded as
number, where the number is given in binary and the
number is a binary representation of a float (IEEE 754).

Since the GPIO expander is configured with a weak
pullup and closing a jumper will cause a low logic
level to occur, the input to the expander is inverted.
The input for a proper scaling coefficient is:
11110101 binary

The students only have to encode the float number in binary
representation. The float number is a calibration coefficient
that will convert voltage to a radiation flux. A binary 1 is
represented by a jumper. A binary 0 is represented by an
absence of a jumper.

The students only have to encode the scaling byte in
binary representation. A binary 1 is represented by a
jumper. A binary 0 is represented by an absence of a
jumper.

(c) 2019-2020 nj kinar
Design License CERN OHL
Open Hardware
http://cern.ch/cern-ohl

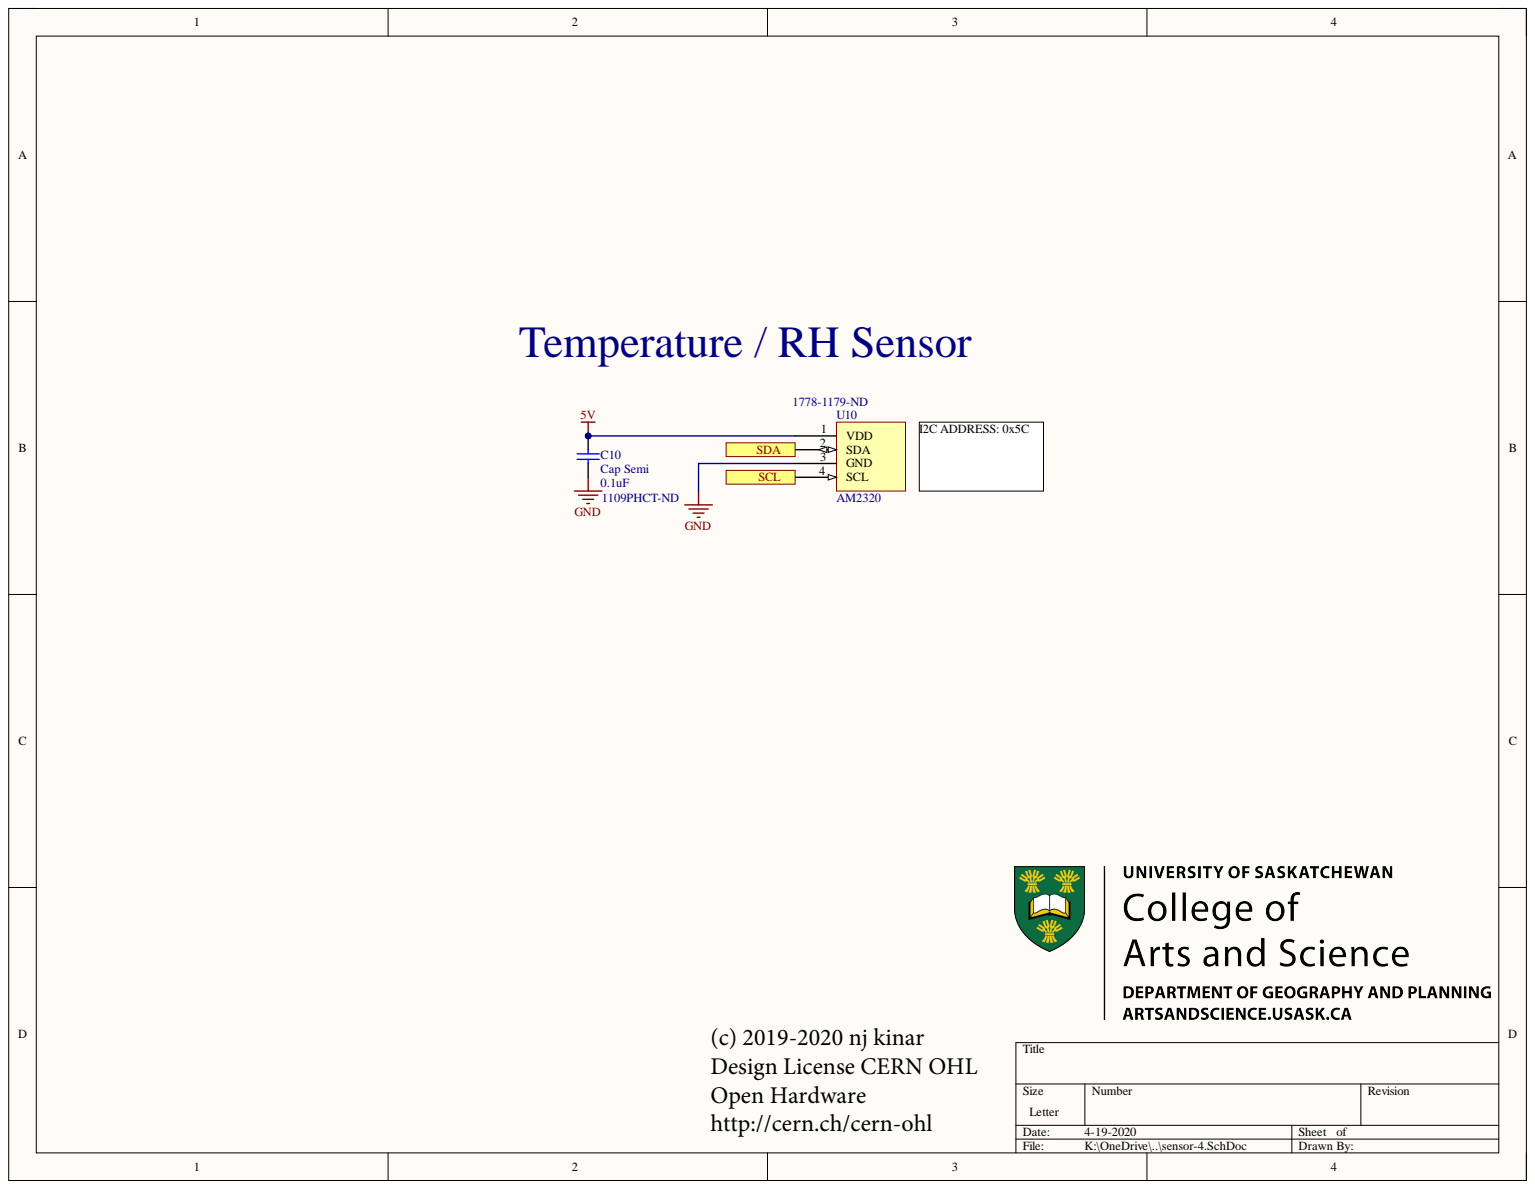
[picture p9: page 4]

SDA 2

SCL 4

(c) 2019-2020 nj kinar
Design License CERN OHL
Open Hardware

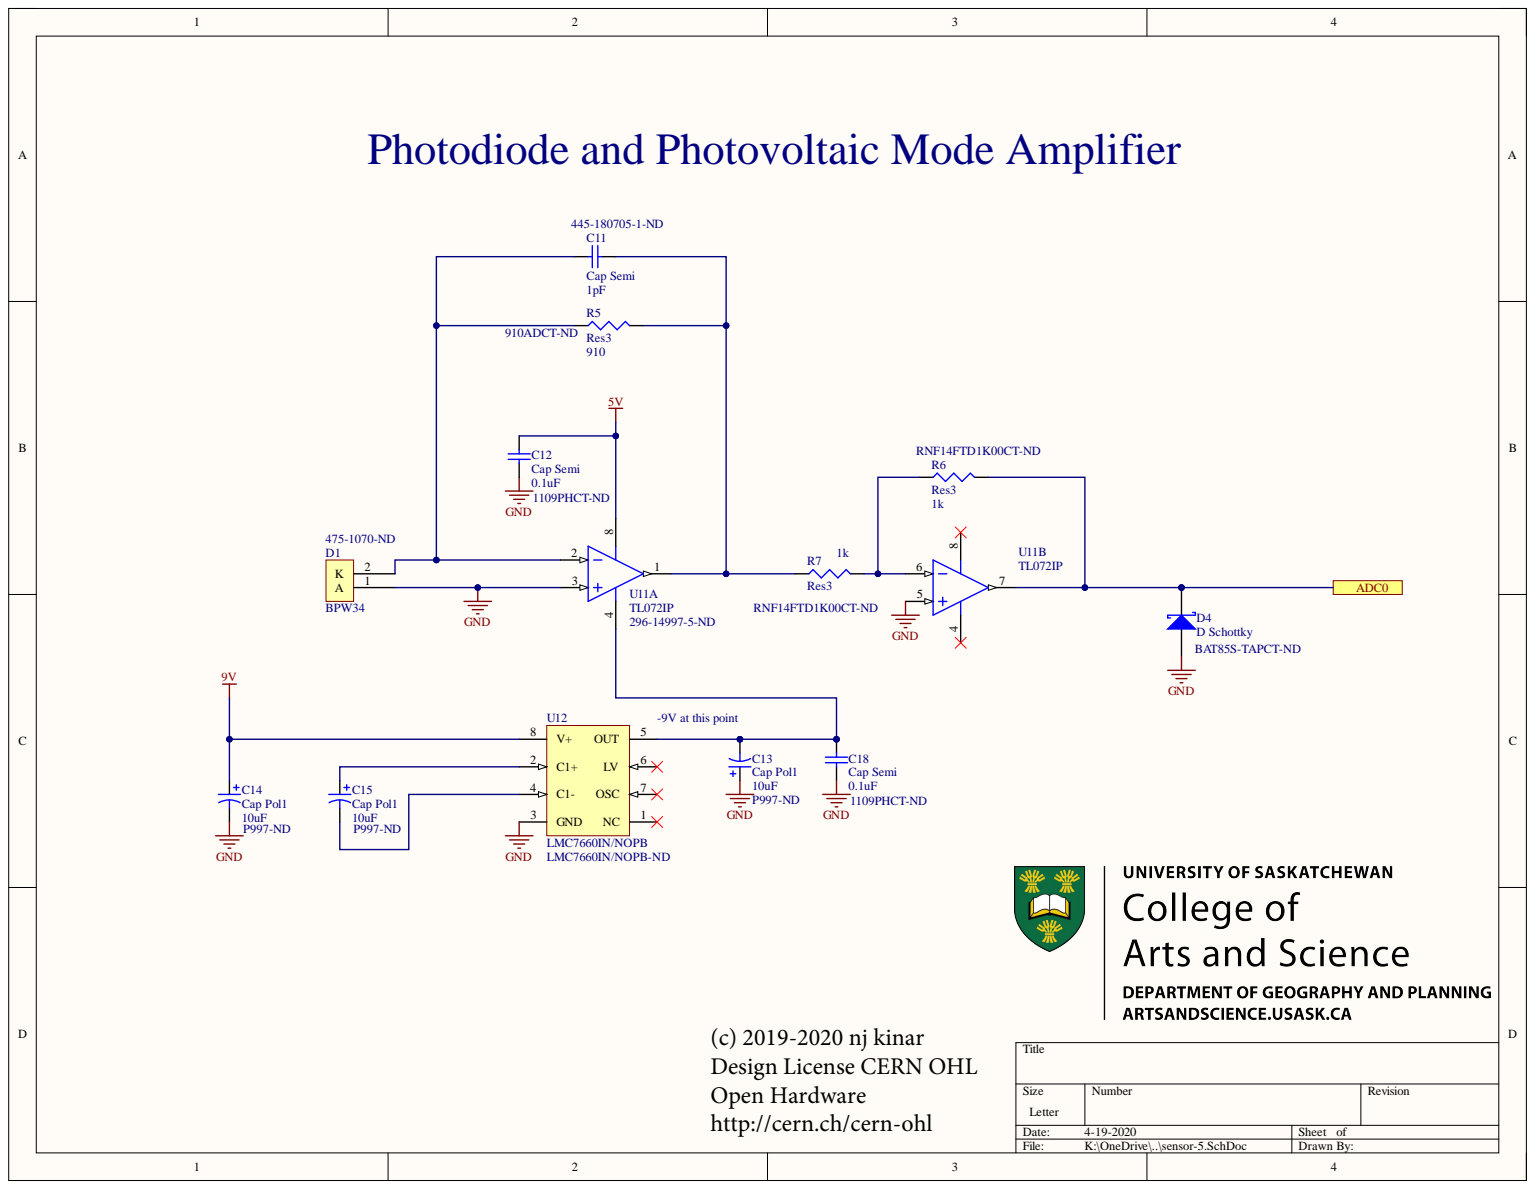
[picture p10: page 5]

Photodiode and Photovoltaic Mode Amplifier

Cap Pol1 10uF P997-ND | GND 3

(c) 2019-2020 nj kinar
Design License CERN OHL
Open Hardware

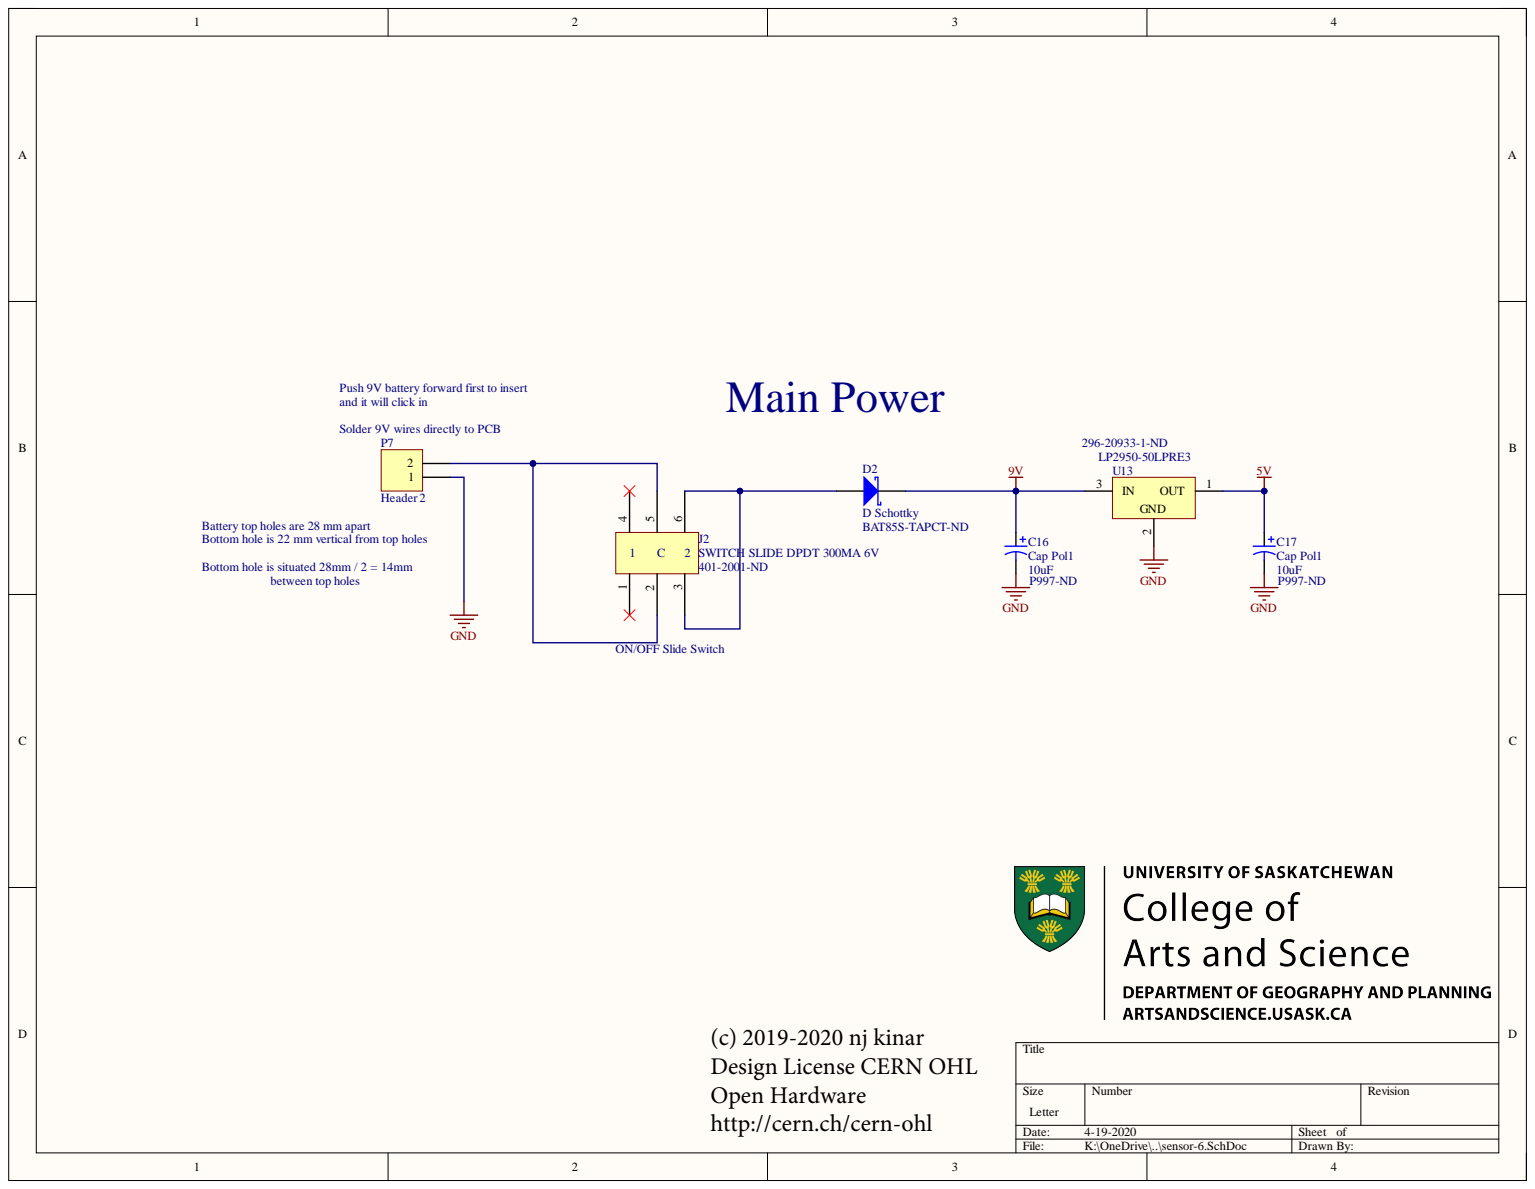
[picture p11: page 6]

Push 9V battery forward first to insert
and it will click in

Solder 9V wires directly to PCB

Battery top holes are 28 mm apart
Bottom hole is 22 mm vertical from top holes

Bottom hole is situated 28mm / 2 = 14mm

ON/OFF Slide Switch

(c) 2019-2020 nj kinar
Design License CERN OHL
Open Hardware

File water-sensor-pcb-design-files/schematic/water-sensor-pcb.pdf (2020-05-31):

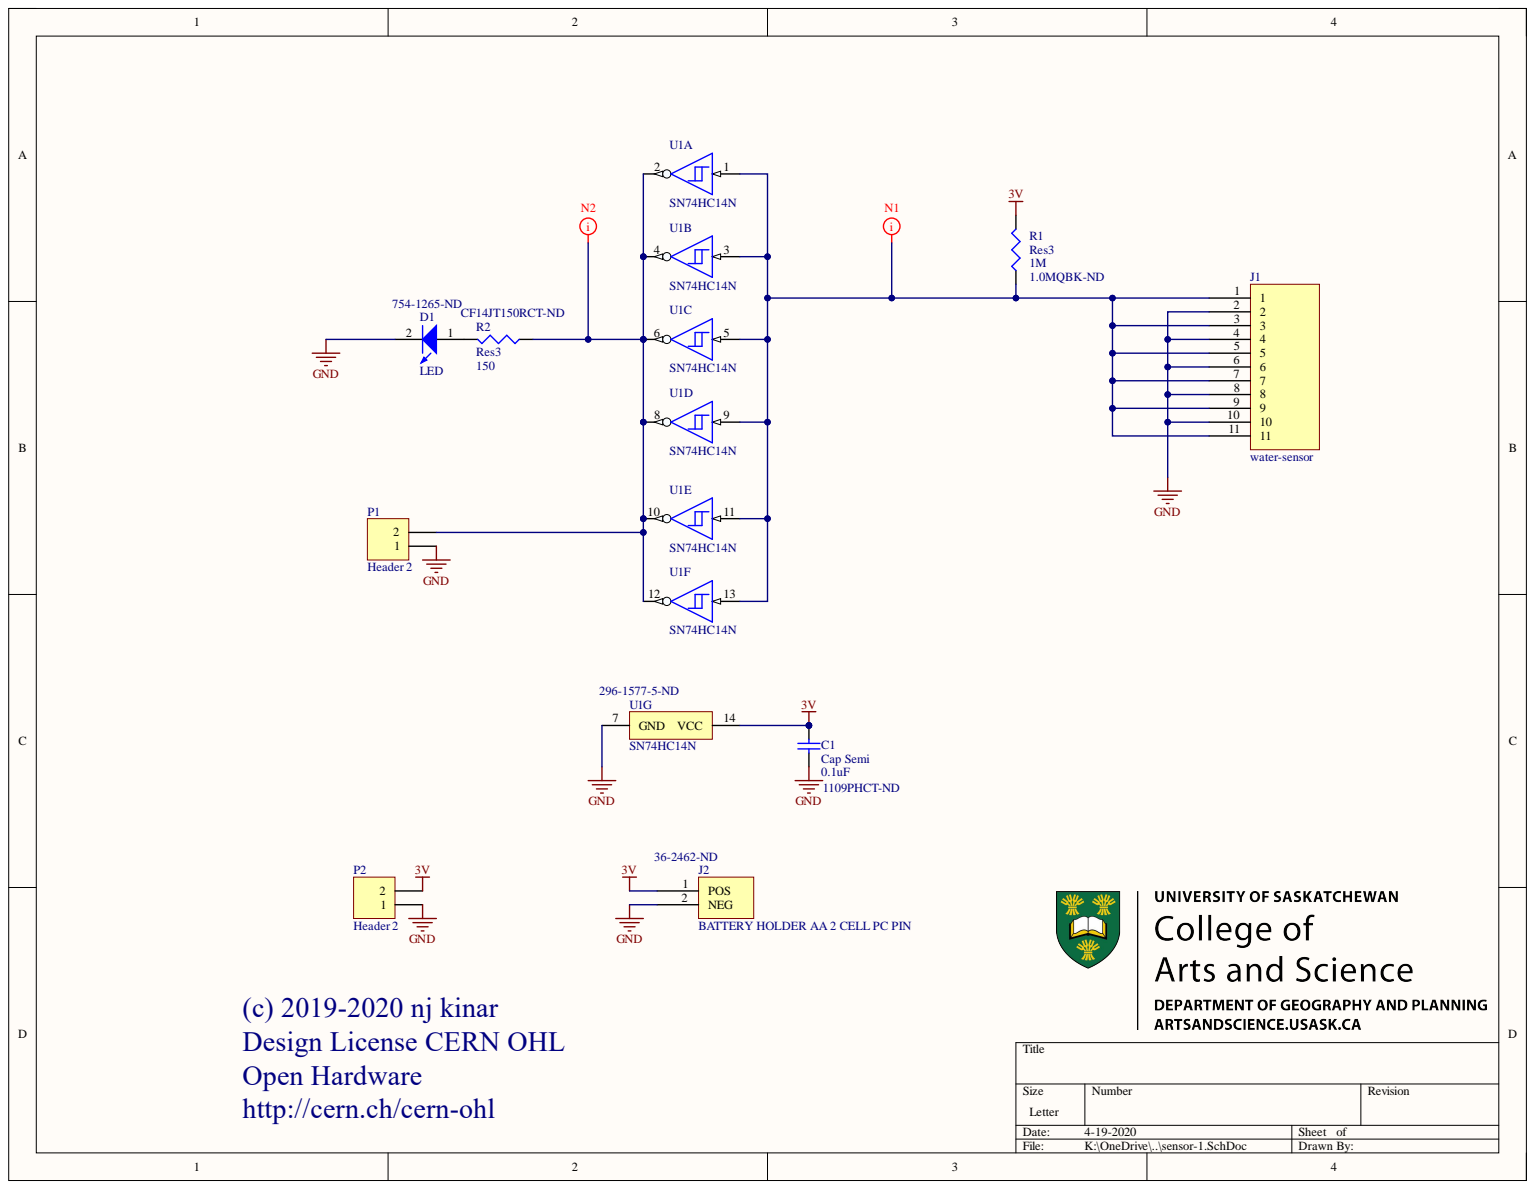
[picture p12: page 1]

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
10 10

Header 2
(c) 2019-2020 nj kinar
Design License CERN OHL
Open Hardware
http://cern.ch/cern-ohl

BATTERY HOLDER AA 2 CELL PC PIN

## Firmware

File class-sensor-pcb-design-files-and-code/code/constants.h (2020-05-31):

/* 
 * This file is part of the class sensor code for the
 * "Introducing Electronic Circuits and Hydrological
 * Models to Postsecondary Physical Geography Students: 
 * Systems Science, Circuit Theory, Construction and Calibration" paper
 * 
 * Copyright (c) 2019-2020 Nicholas J. Kinar
 * 
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
 * You should have received a copy of the GNU General Public License 
 * along with this program. If not, see <http://www.gnu.org/licenses/>.
 */

#pragma once

// DEFINES
#define F_CPU   8000000UL			// 8 MHz clock

#define USE_GPIO						// turn on this define to use GPIO to obtain coefficients (for student boards)

// #define DEBUG_BOARD					// turn on this define to debug the board and allow for serial port access
// #define PRINT_DEBUG_STARTUP_I2C		// turn on this define to print the startup I2C information
// #define FORCE_PYRO					// turn on this define to force pyranometer mode on a fully-populated board

// Addresses
#define T_RH_ADDR	0x5C			// T-RH sensor
#define GPIO8_ADDR	0x20			// 8-bit GPIO expander address
#define GPIO16_ADDR_LOW		0x21	// low word 16-bit expander
#define GPIO16_ADDR_HIGH	0x22	// high word 16-bit expander
	
#define ADC_AVERAGE_TIMES	25
#define VREF				5.0f

#define HIGH	1
#define LOW		0

#define BAUD_UART  9600UL   // 9600 baud uart
#define BAUDRATE_UART ((F_CPU)/(BAUD_UART*16UL)-1)
#define UART_USB_NUM	0

#define UART_BUFFER_SIZE   16
#define SERIAL_BUFFER_SIZE   16

#define MAX_DISPLAY_BYTES	9
#define FIRST_LINE_DISPLAY  0
#define SECOND_LINE_DISPLAY  1

#define CRLF "\r\n"
#define CR '\r'
#define LF '\n'
#define BACKSPACE '\b'
#define SPACE ' '
#define STR_TERMINATOR '\0'
#define PROMPT ">"
#define LT  CR

#define ERROR_STRING   "ERROR"
#define DONE_STRING    "DONE"
#define TRUE_STRING		"TRUE"
#define FALSE_STRING	"FALSE"

#define SCL_CLK		100000			// 100 kHz clock for I2C

#define T_RH_SCALE		10			// scaling coefficient for temperature
#define PYR_SCALE		156.3f		// scaling coefficient for pyranometer

// COMMANDS
#define INFO_COMMAND	"info"
#define HW_COMMAND		"hw"
#define TRH_COMMAND		"trh"
#define VFX_COMMAND		"vfx"
#define RT_COMMAND		"rt"
#define P8_COMMAND		"p8"
#define P32_COMMAND		"p32"
#define CP_COMMAND		"cp"
#define SW_COMMAND		"sw"
#define ADC_COMMAND		"adc"
#define CD_COMMAND		"cd"
#define ON_TIMER_COMMAND	"on-timer"
#define OFF_TIMER_COMMAND	"off-timer"
#define ITO_COMMAND			"ito"
#define SET_FLOAT_COMMAND	"sf"
#define WELCOME_COMMAND		"welcome"

// MACROS
#define BIT_SET(a,b) ((a) |= (1ULL<<(b)))
#define BIT_CLEAR(a,b) ((a) &= ~(1ULL<<(b)))
#define BIT_FLIP(a,b) ((a) ^= (1ULL<<(b)))
#define BIT_CHECK(a,b) (!!((a) & (1ULL<<(b))))

#define BYTE_TO_BINARY_PATTERN "%c%c%c%c%c%c%c%c"
#define BYTE_TO_BINARY(byte)  \
(byte & 0x80 ? '1' : '0'), \
(byte & 0x40 ? '1' : '0'), \
(byte & 0x20 ? '1' : '0'), \
(byte & 0x10 ? '1' : '0'), \
(byte & 0x08 ? '1' : '0'), \
(byte & 0x04 ? '1' : '0'), \
(byte & 0x02 ? '1' : '0'), \
(byte & 0x01 ? '1' : '0')

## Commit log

2020-05-31 Initial checkin of files
    [class-sensor.GBL, class-sensor.GBO, class-sensor.GBP, class-sensor.GBS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]
2020-06-01 Delete sensor-1.SchDocPreview
    Unecessary file removal

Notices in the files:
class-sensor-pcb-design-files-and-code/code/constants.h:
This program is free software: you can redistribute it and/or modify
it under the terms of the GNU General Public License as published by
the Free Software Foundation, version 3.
